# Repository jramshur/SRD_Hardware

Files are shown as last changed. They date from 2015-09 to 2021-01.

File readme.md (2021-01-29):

# SRD Hardware

The simultaneous stimulation-and-recording device (SRD) is a wearable, wireless brain-computer interface system designed to train cortical circuits in awake rats. This repository contains design files for the SRD hardware including Eagle PCB files and 3D design files for the enclosure.

Software and firmware for this hardware system can be found in the following repositories:

- https://github.com/jramshur/SRD_Firmware
- https://github.com/jramshur/SRD_GUI

## Description

The simultaneous stimulation-and-recording device (SRD) is a Bluetooth wireless brain-computer interface system designed for use in awake rats. This repository contains design files for the SRD hardware including Eagle PCB files and 3D design files for the enclosure.

### Features
- Cypress Semiconductor PSoC 3 System-on-a-Chip 
- Intan Technologies digital electrophysiology interface chip
- more ...

### System Overview







## Wiki Navigation

* [Home][home]
* [Circuit Design][circuit]
* [PCB Design][pcb]
* [Enclosure][enclosure]
* [Battery][battery]
* [Programming Adaptor][adaptor]

[home]: https://github.com/jramshur/SRD_Hardware/wiki/Home
[circuit]: https://github.com/jramshur/SRD_Hardware/wiki/Circuit
[pcb]: https://github.com/jramshur/SRD_Hardware/wiki/PCB
[enclosure]: https://github.com/jramshur/SRD_Hardware/wiki/Enclosure
[battery]: https://github.com/jramshur/SRD_Hardware/wiki/Battery
[adaptor]: https://github.com/jramshur/SRD_Hardware/wiki/Programming-Adaptor

## Contact Info

John T. Ramshur, PhD  
jramshur@gmail.com  
LinkedIn: [http://www.linkedin.com/in/johnramshur](http://www.linkedin.com/in/johnramshur)  
Blog: [http://www.johnramshur.com](http://www.johnramshur.com)

**Project was part of my PhD work while at:**

Joint Program in Biomedical Engineering  
[University of Memphis](http://www.memphis.edu/bme/)  
[University of Tennessee Health Science Center](http://www.uthsc.edu/bme/)  
Advisor: Amy de Jongh Curry, PhD

Department of Anatomy and Neurobiology  
[University of Tennessee Health Science Center](https://www.uthsc.edu/anatomy-neurobiology/)  
Advisor: Robert S. Waters, PhD

## License

GNU General Public License 3.0

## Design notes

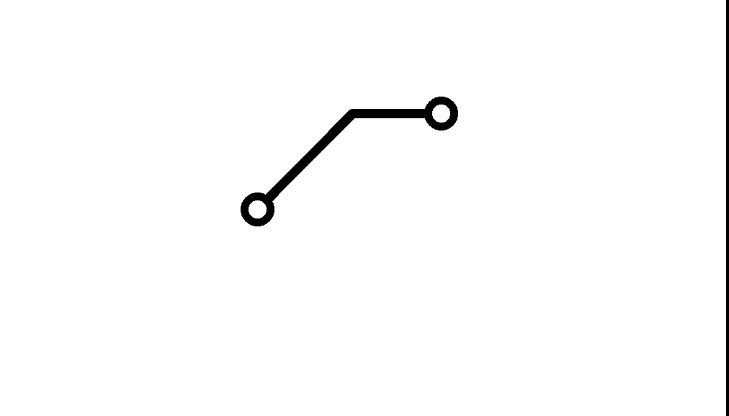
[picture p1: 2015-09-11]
Programming_Adaptor_PCB/eagleUp/.@__thumb/s800eagleUp_PSOC_10pin_to_ZIF_bottom.png

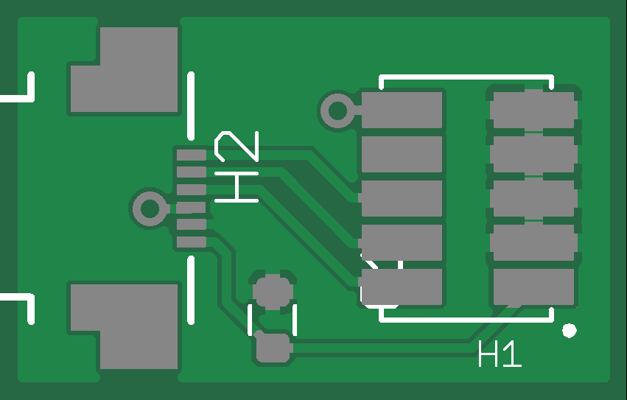
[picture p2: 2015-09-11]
Programming_Adaptor_PCB/eagleUp/.@__thumb/defaulteagleUp_PSOC_10pin_to_ZIF_board_top.png

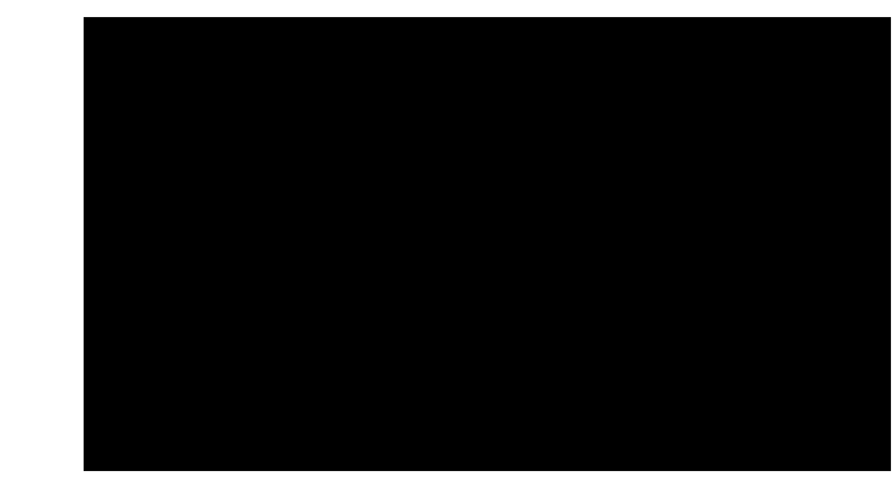
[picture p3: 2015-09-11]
SRD_PCB/eagleUp/eagleUp_SRD_imagesize.png

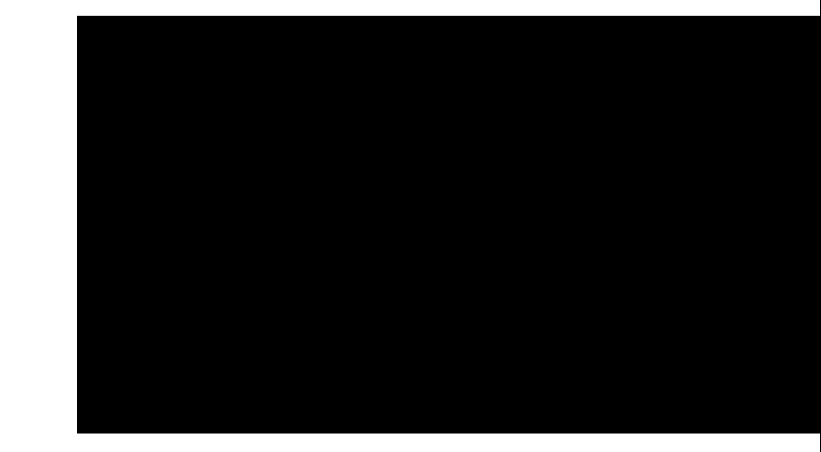
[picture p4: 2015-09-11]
SRD_PCB/eagleUp/.@__thumb/s800eagleUp_SRD_imagesize.png

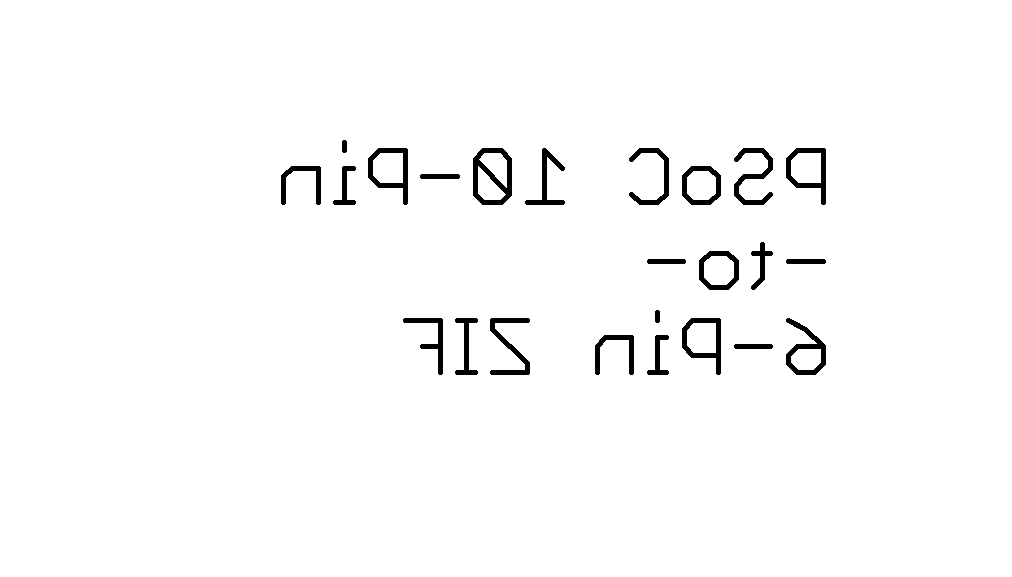
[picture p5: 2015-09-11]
Programming_Adaptor_PCB/eagleUp/eagleUp_PSOC_10pin_to_ZIF_bottom_silk.png

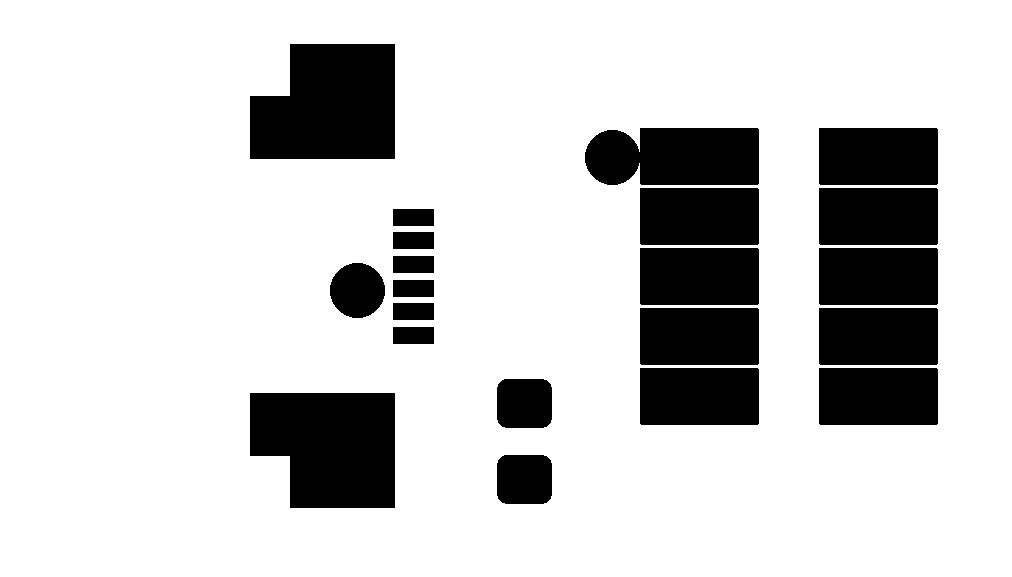
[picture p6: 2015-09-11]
Programming_Adaptor_PCB/eagleUp/eagleUp_PSOC_10pin_to_ZIF_top_mask.png

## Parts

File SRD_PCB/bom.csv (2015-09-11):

Qty | Value | Device | Package | Parts | Description | MF | MPN | OC_FARNELL | OC_NEWARK | PACKAGE | SUPPLIER
1 |  | LED | CHIPLED_0603 | LED1 | LED
1 |  | PHOTOTRANSISTOR | MTD8000M3B-T | Q1 | phototransistor
11 | 0.1uF | CC0402-N | CAPC1005X55N | C20
4 | 0.1uF | CC0603-N | CAPC1608X90N | C7
1 | 10nF | CC0402-N | CAPC1005X55N | C41 | Capacitor (english/metric) cermaic capacitor nominal landpattern (N).
6 | 10uF | CC0805-N | CAPC2012X100N | C12
4 | 1k | RR0402-N | RESC1005X35N | R23
2 | 1uF | CC0402-N | CAPC1005X55N | C23
4 | 1uF | CC0603-N | CAPC1608X90N | C1
1 | 1uF | CC0805-N | CAPC2012X100N | C31 | Capacitor (english/metric) cermaic capacitor nominal landpattern (N).
2 | 2.2uF | CC0603-N | CAPC1608X90N | C5
2 | 220nF | CC0402-N | CAPC1005X55N | C8
2 | 3.3uF | CC0805-N | CAPC2012X100N | C10
4 | 4.7k | RR0402-N | RESC1005X35N | R20
2 | 52746-6 | 52746-6 | 52746-6 | AUX
1 | A79043-001 | A79043-001 | OMNETCS-18PIN-SMD | H10 | Omnetics 18 Position Dual Row Female Nano-Miniature (.025/.64mm) Connector. Featuring 2 Guide Posts Holes and Vertical Surface Mount Tails."
2 | ALD1105 | ALD1105 | SO14MIN | U7
1 | AS1302BGA | AS1302BGA | BGA9C40P3X3_121X121X63B27N | U2
1 | CY8C3866 | CY8C3866 | QFN68_8MM_0.4PITCH | U4
1 | DG9409DN-T1-E4 | DG9409DN-T1-E4 | QFN65P400X400X100-17N | U9 | Analog Multiplexers |  | DG9409DN-T1-E4 | - | 65K2483 | QFN-16 | VISHAY SILICONIX
1 | DIODE | DIODE | DO-216AA | D2 | Diode
1 | LED_RGB | LED_RGB | LED_RGB | RGB1 | Kignbright APTF1616SEJ3ZGGVBDC
1 | MAX865 | MAX865 | UMAX8 | U3
1 | MIC5392/3 | MIC5392/3 | THIN_DFN | U1 | Micrel High-Performance Dual 150mA LDO
1 | PHOTOTRANSISTOR_D | PHOTOTRANSISTOR_D | OP501 | Q2
1 | RHD2216 | RHD2216 | RHD2000 | U6
1 | RN42 | RN42 | RN42 | U5 | Microchip (Roving Networks) RN42 Bluetooth module with antena.
4 | SOLDERJUMPERNO | SOLDERJUMPERNO | SJ_2S-NO | SJ1
1 | SPST_TACT-KMR2 | SPST_TACT-KMR2 | KMR2 | SW1 | SMT 6mm switch
4 | TEST-POINT | TEST-POINT | PAD1MMX1MM | TP10+
1 | USB | USB | USB-MICRO-B-TH | BAT | USB Micro-B Plug

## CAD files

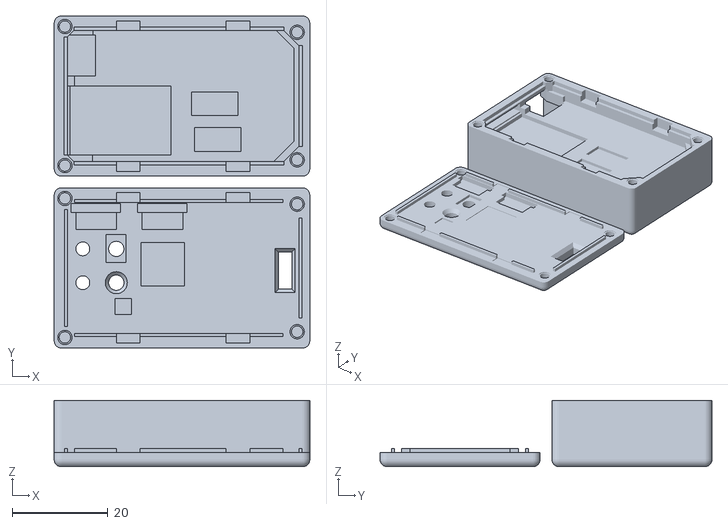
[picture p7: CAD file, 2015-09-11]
enclosure/SRD_revB_caseOnly_for3DPrinting.stl
53.5 x 69.5 x 13.9

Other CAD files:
Programming_Adaptor_PCB/PSOC_10pin_to_ZIF.skp

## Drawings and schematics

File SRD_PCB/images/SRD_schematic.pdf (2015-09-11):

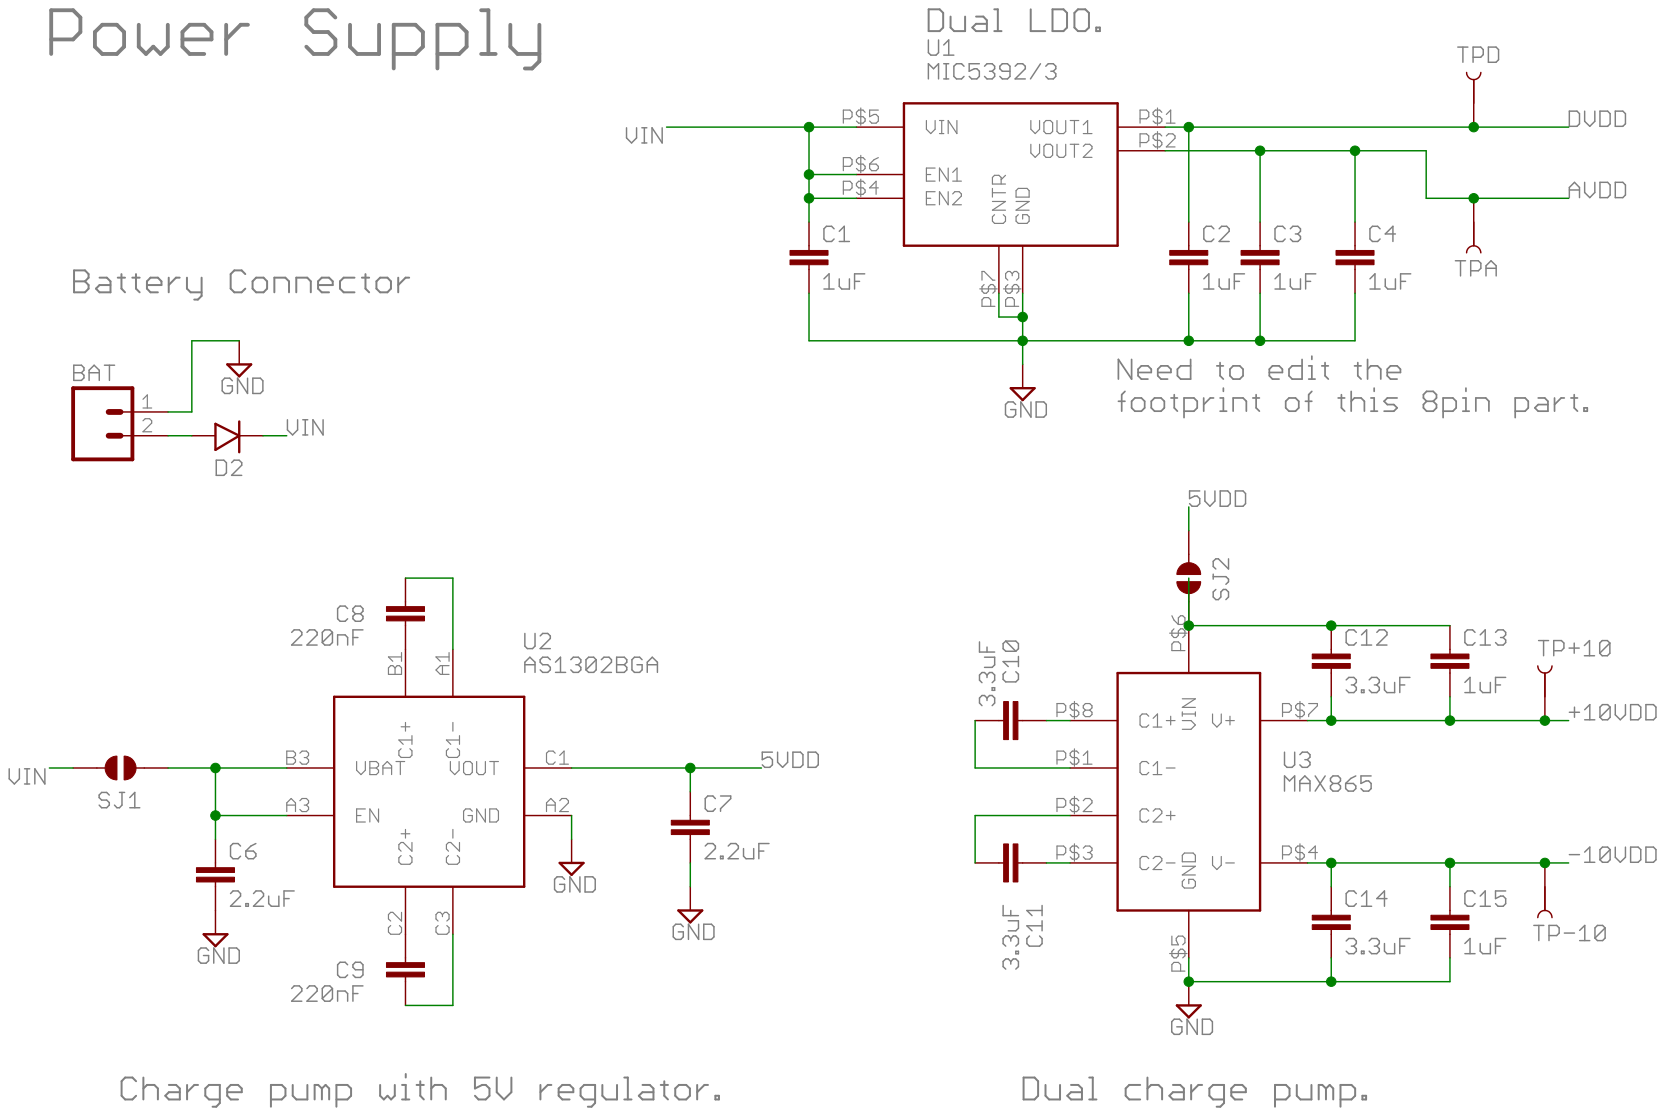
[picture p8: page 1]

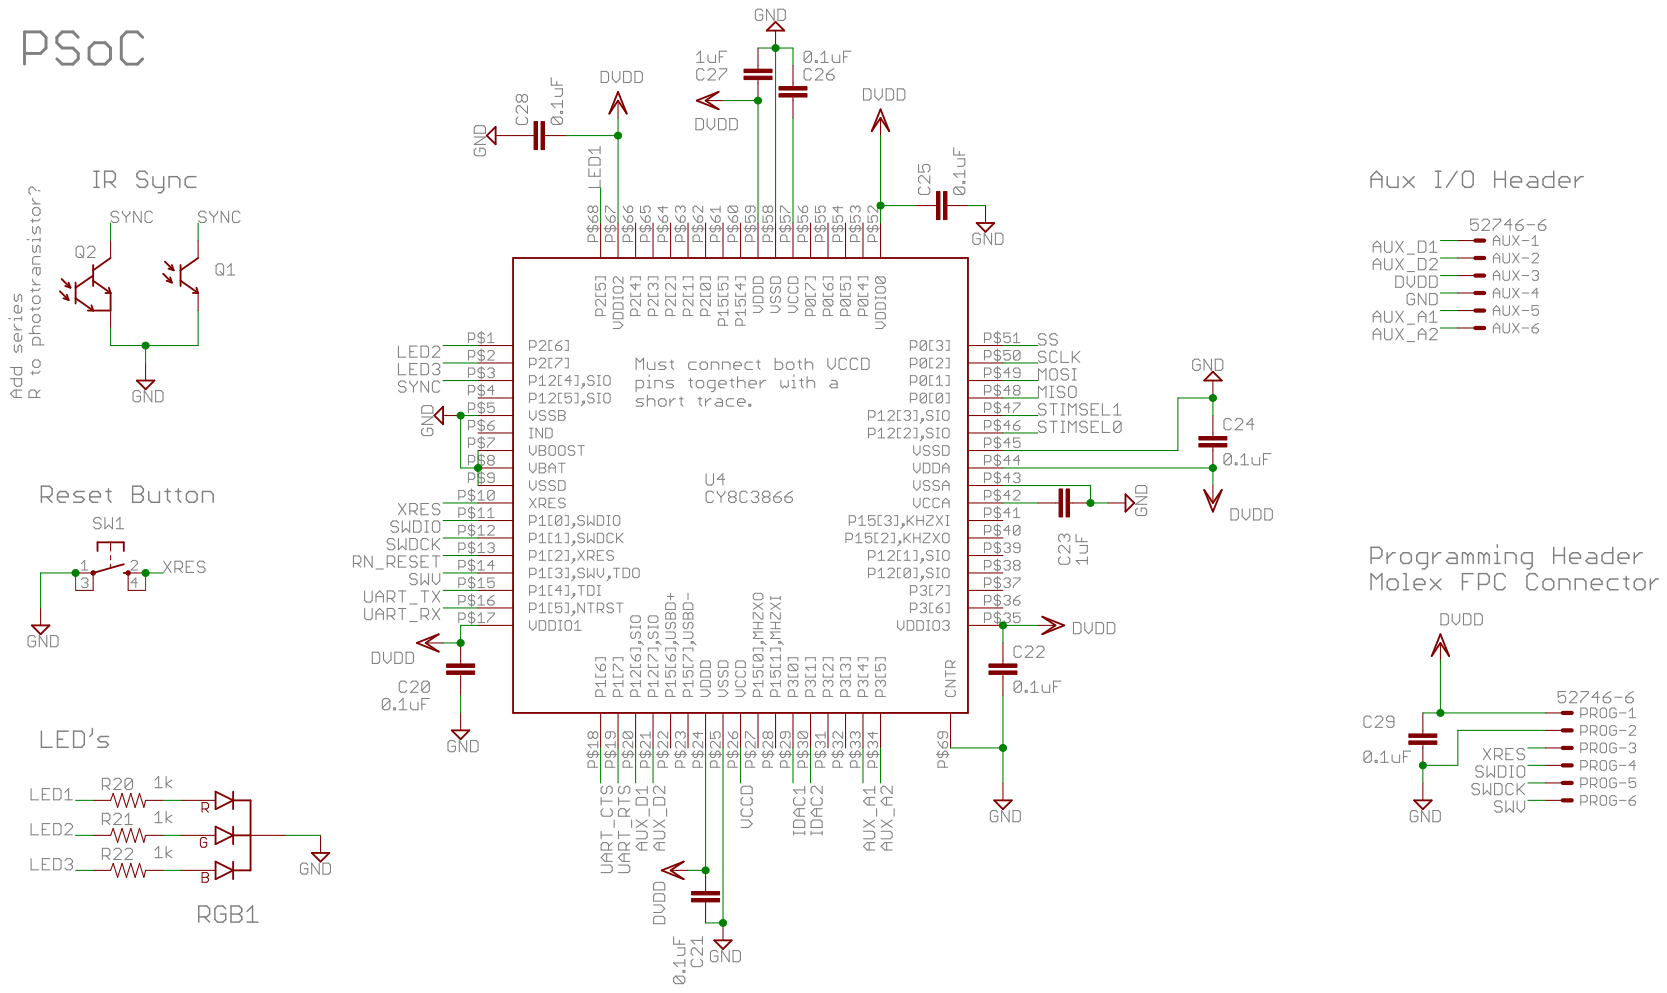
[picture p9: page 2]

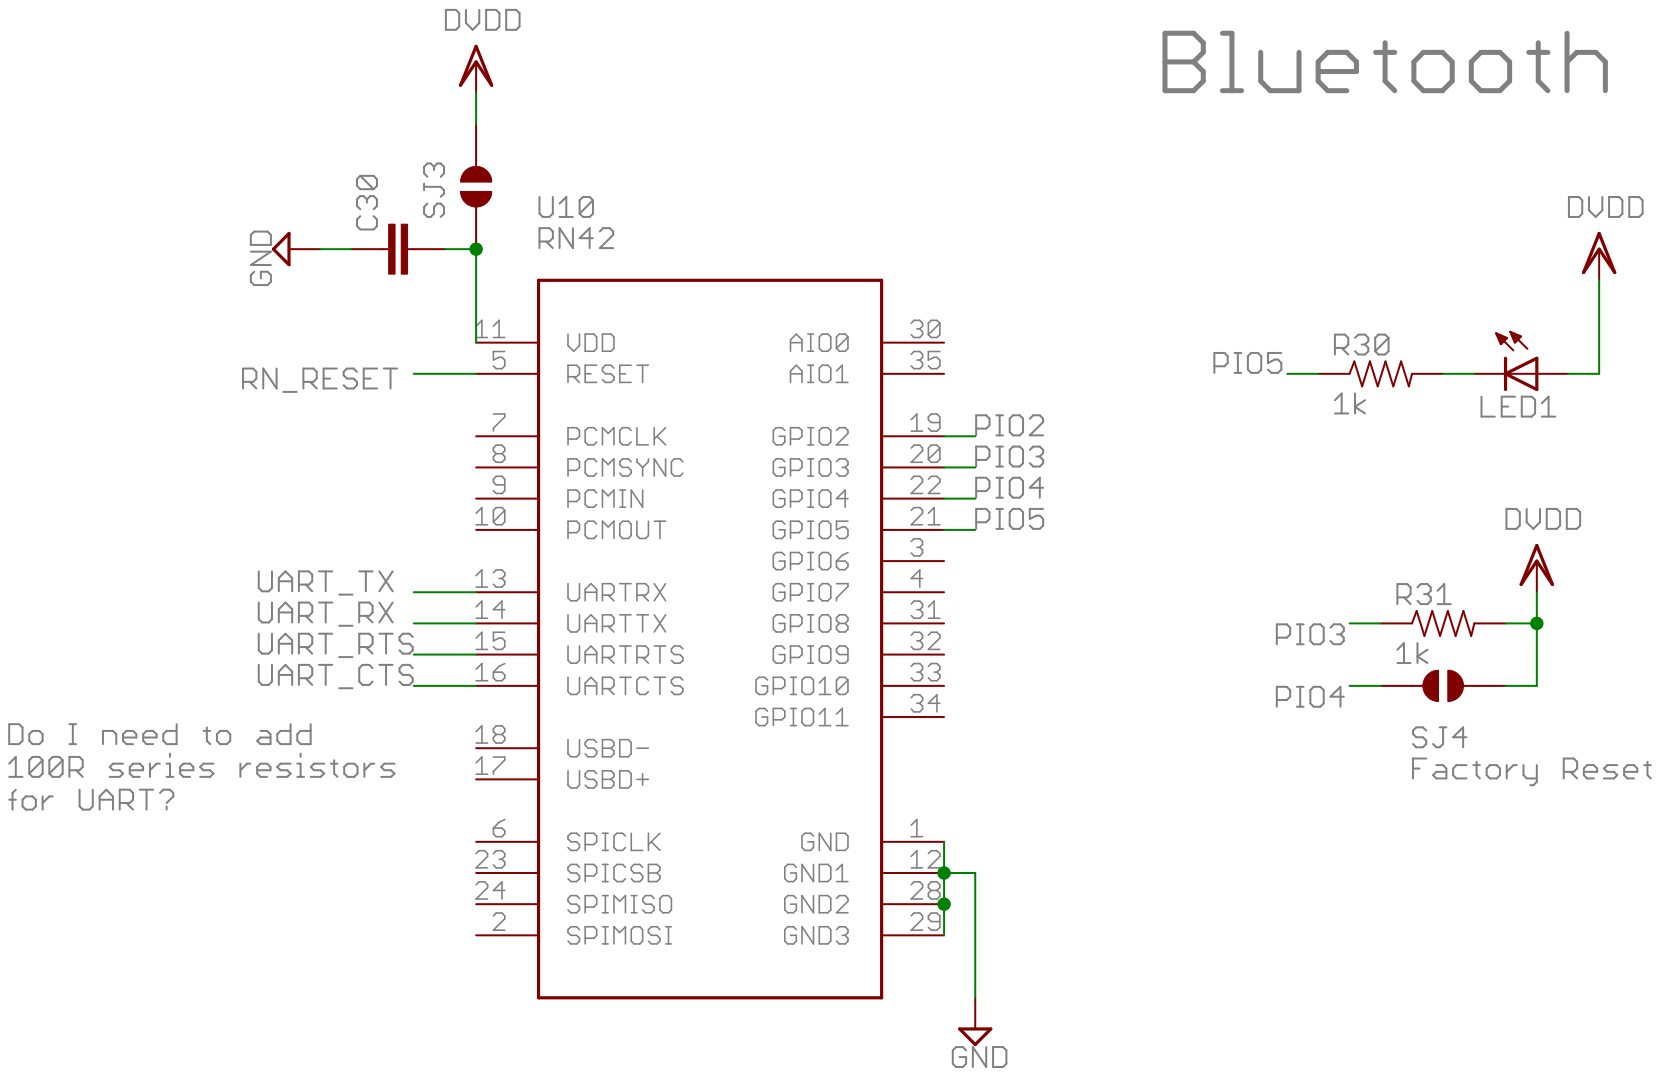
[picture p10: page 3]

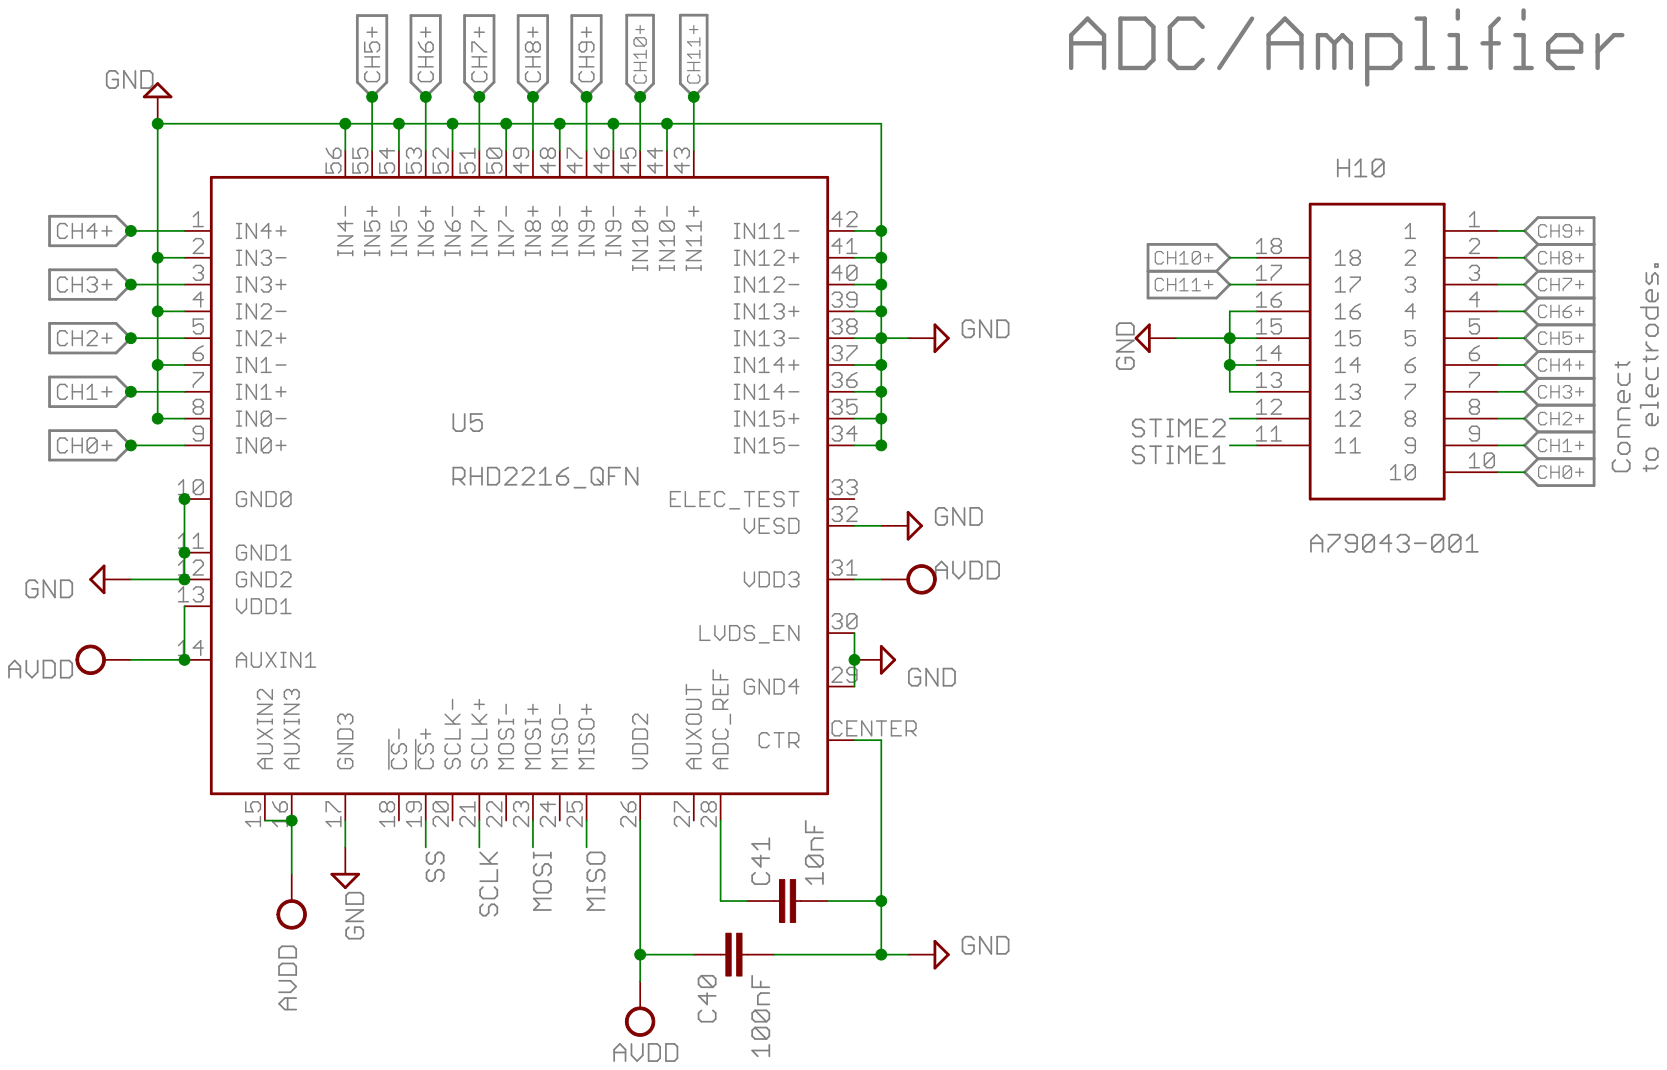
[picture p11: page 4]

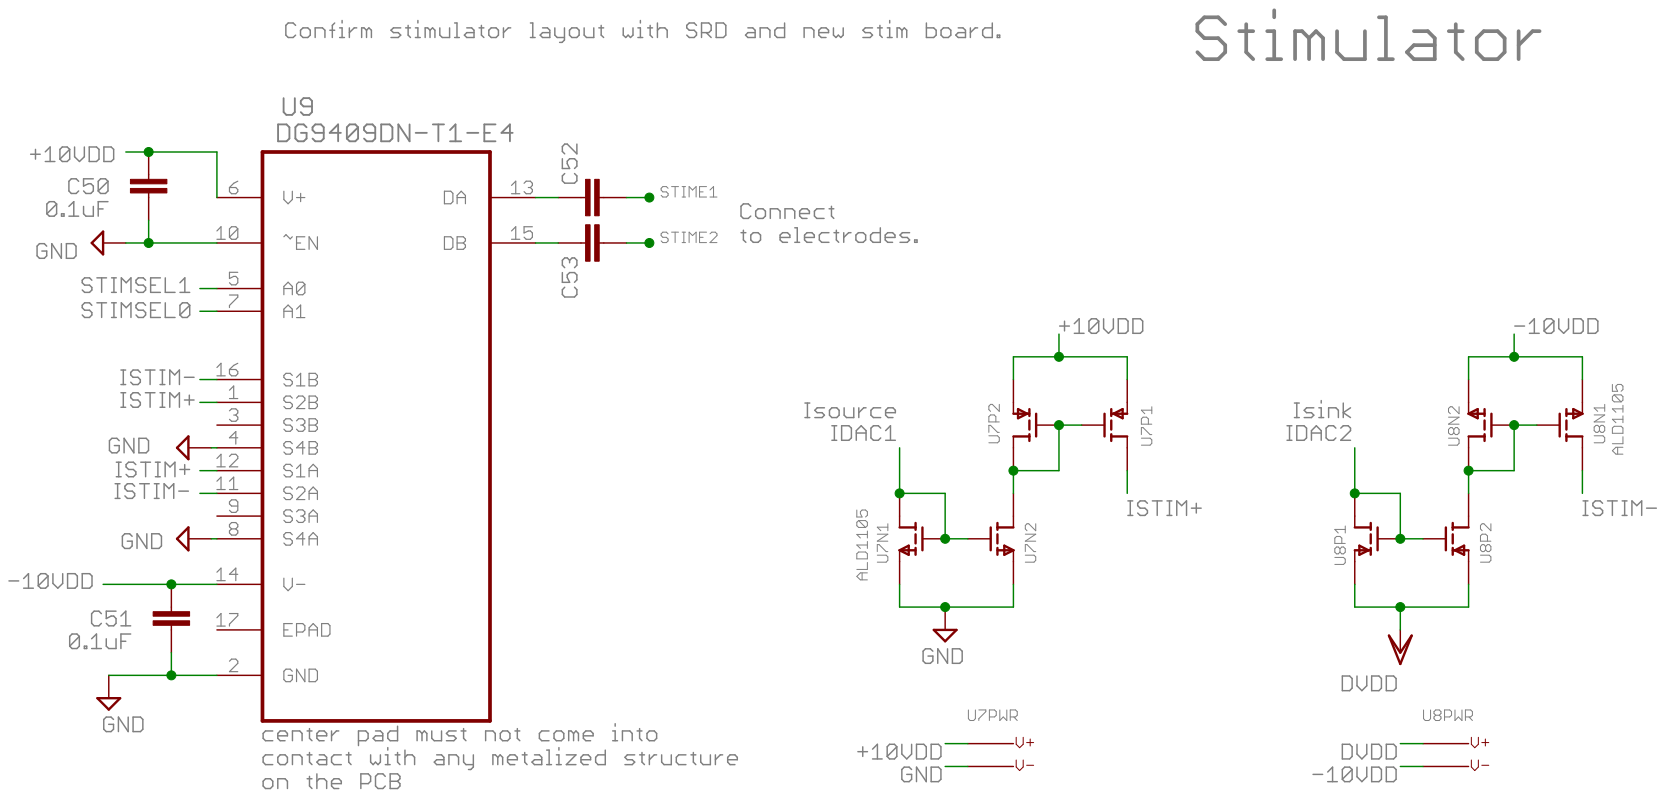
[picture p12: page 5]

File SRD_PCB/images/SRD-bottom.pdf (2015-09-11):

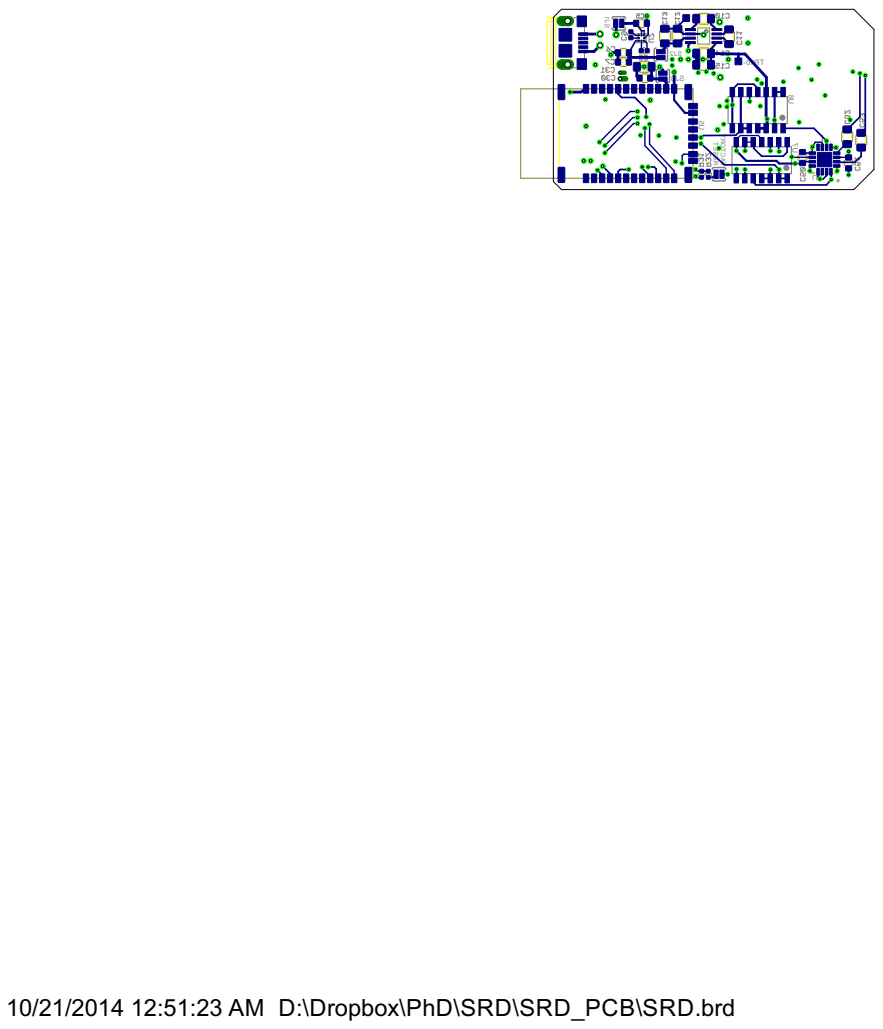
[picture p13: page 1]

10/21/2014 12:51:23 AM D:\Dropbox\PhD\SRD\SRD_PCB\SRD.brd

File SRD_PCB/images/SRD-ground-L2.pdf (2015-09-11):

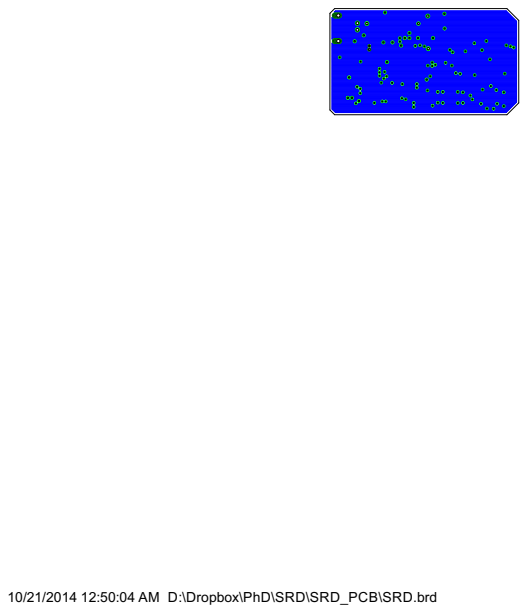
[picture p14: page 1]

10/21/2014 12:50:04 AM D:\Dropbox\PhD\SRD\SRD_PCB\SRD.brd

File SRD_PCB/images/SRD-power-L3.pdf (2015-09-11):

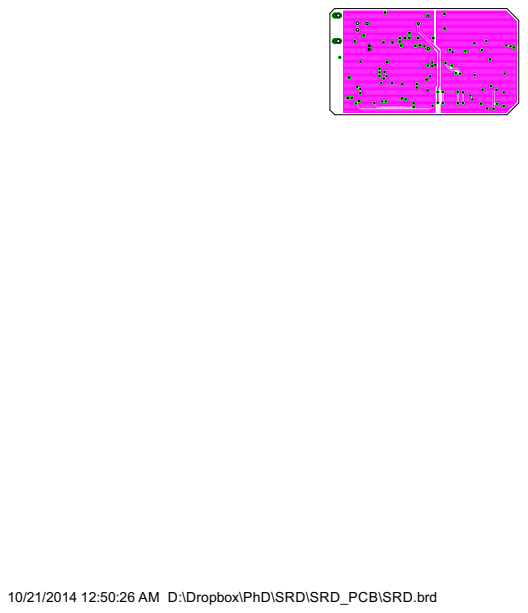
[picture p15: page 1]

10/21/2014 12:50:26 AM D:\Dropbox\PhD\SRD\SRD_PCB\SRD.brd

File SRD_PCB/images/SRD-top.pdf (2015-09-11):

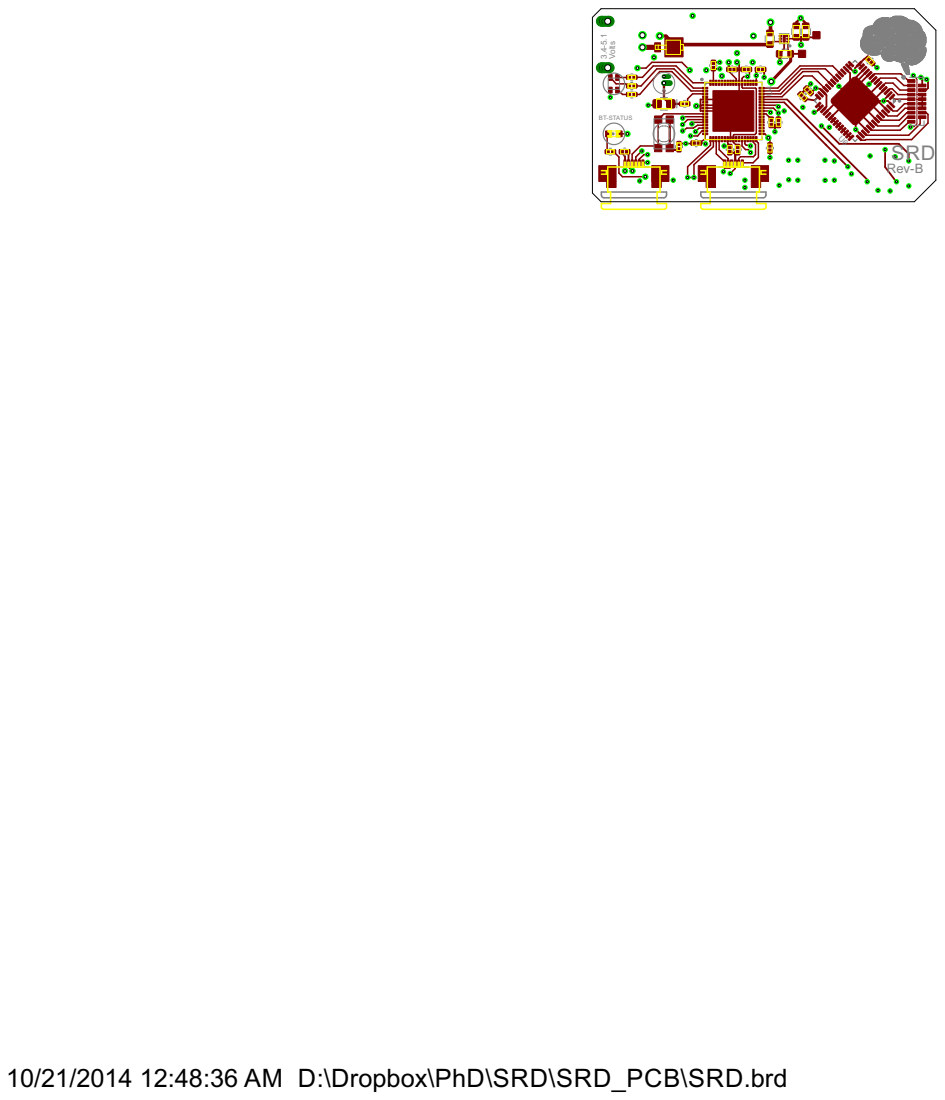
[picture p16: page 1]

10/21/2014 12:48:36 AM D:\Dropbox\PhD\SRD\SRD_PCB\SRD.brd

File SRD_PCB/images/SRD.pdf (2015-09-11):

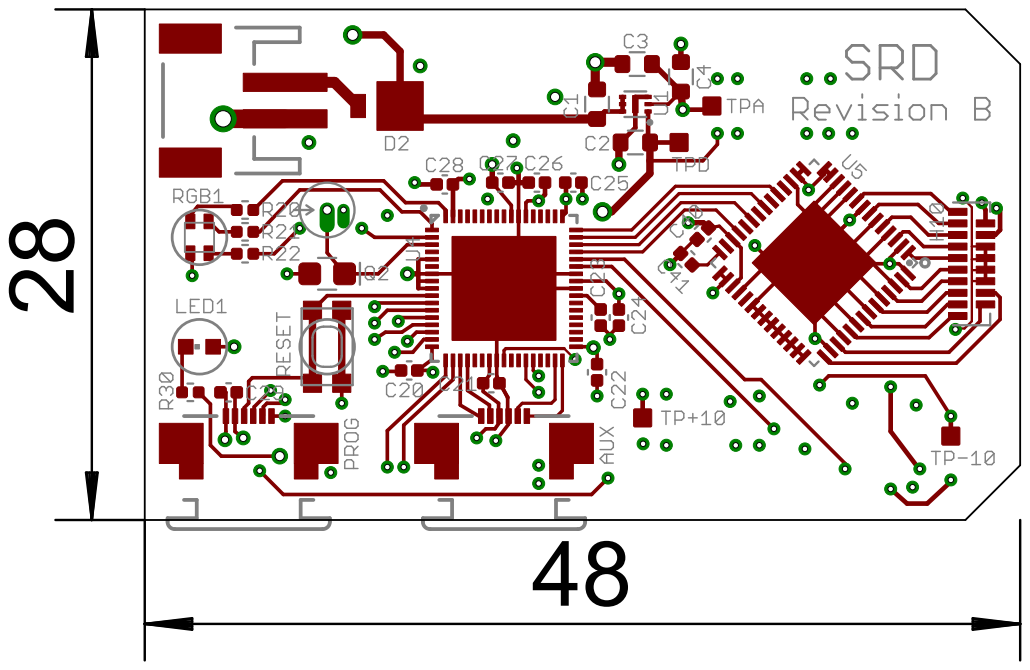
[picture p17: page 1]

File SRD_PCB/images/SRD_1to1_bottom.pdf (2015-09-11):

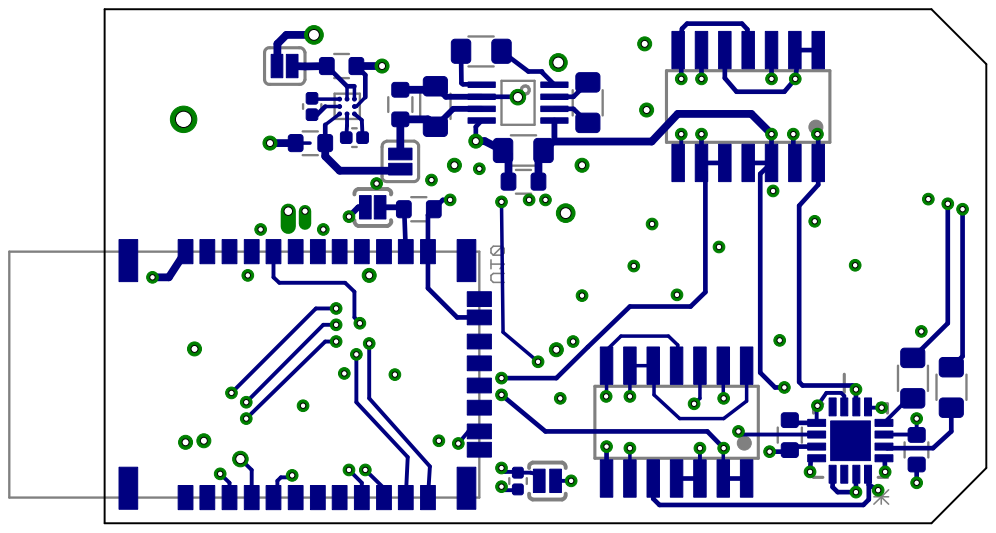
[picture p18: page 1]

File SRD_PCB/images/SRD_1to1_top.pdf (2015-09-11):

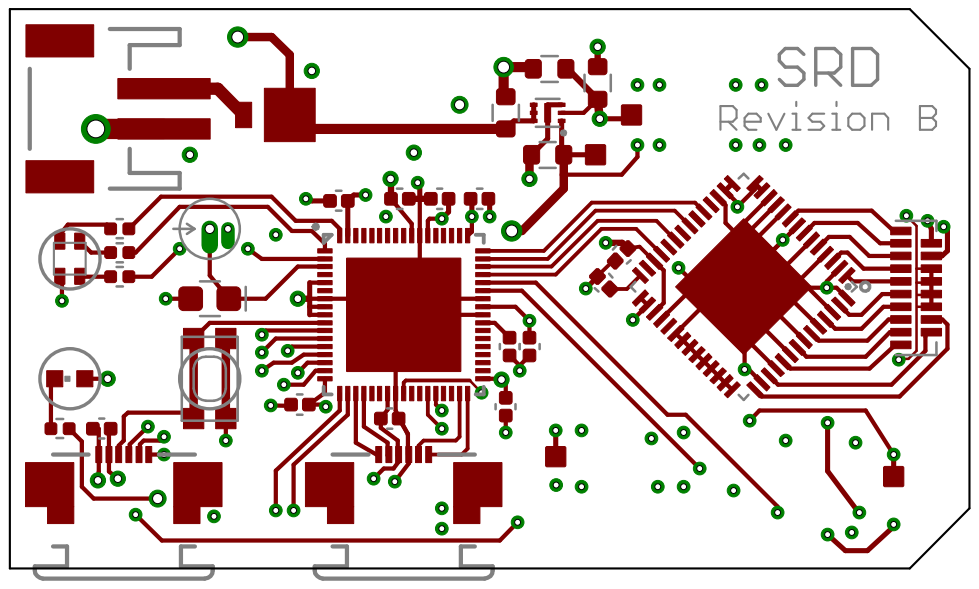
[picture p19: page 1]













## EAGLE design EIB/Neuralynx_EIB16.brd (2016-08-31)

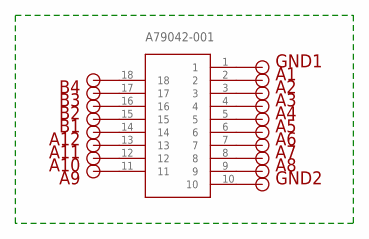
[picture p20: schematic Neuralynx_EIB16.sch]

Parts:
A1, A2, A3, A4, A5, A6, A7, A8, A9, A10, A11, A12: VIA_20MILL; VIA_20MIL
A79042-001: A79043-001; OMNETCS-18PIN-SMD
B1, B2, B3, B4: VIA_20MILL; VIA_20MIL
GND1, GND2: VIA_20MILL; VIA_20MIL

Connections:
unnamed: A79042-001.1, GND1.P$1
unnamed: A79042-001.10, GND2.P$1
unnamed: A8.P$1, A79042-001.9
unnamed: A7.P$1, A79042-001.8
unnamed: A6.P$1, A79042-001.7
unnamed: A5.P$1, A79042-001.6
unnamed: A4.P$1, A79042-001.5
unnamed: A3.P$1, A79042-001.4
unnamed: A2.P$1, A79042-001.3
unnamed: A1.P$1, A79042-001.2
unnamed: A9.P$1, A79042-001.11
unnamed: A10.P$1, A79042-001.12
unnamed: A12.P$1, A79042-001.14
unnamed: A79042-001.15, B1.P$1
unnamed: A79042-001.16, B2.P$1
unnamed: A79042-001.17, B3.P$1
unnamed: A79042-001.18, B4.P$1
unnamed: A11.P$1, A79042-001.13

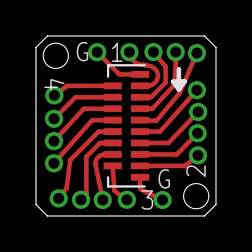
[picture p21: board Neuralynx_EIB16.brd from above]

Board: 2 copper layers, 10.0 x 10.0 mm, 19 parts (0 on the bottom side), 18 nets.

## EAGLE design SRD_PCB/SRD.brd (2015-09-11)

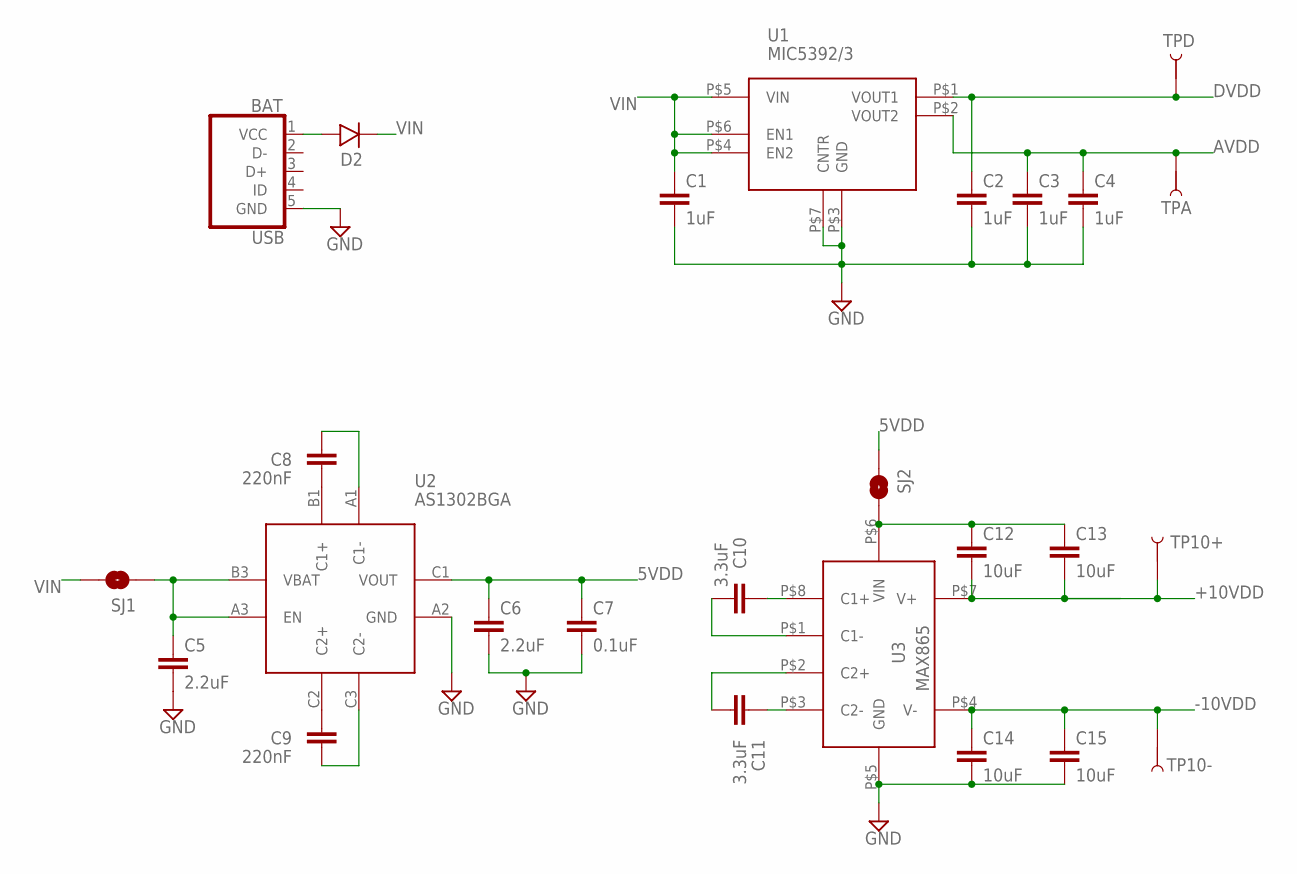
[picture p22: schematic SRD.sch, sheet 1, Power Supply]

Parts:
BAT: USB; USB-MICRO-B-TH
C1, C2, C3, C4: 1uF; CAPC1608X90N
C5, C6: 2.2uF; CAPC1608X90N
C7: 0.1uF; CAPC1608X90N
C8, C9: 220nF; CAPC1005X55N
C10, C11: 3.3uF; CAPC2012X100N
C12, C13, C14, C15: 10uF; CAPC2012X100N
D2: DIODE; DO-216AA
SJ1, SJ2: SOLDERJUMPERNO; SJ_2S-NO
TP10+, TP10-: TEST-POINT; PAD1MMX1MM
TPA: TEST-POINT; PAD1MMX1MM
TPD: TEST-POINT; PAD1MMX1MM
U1: MIC5392/3; THIN_DFN
U2: AS1302BGA; BGA9C40P3X3_121X121X63B27N
U3: MAX865; UMAX8

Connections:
5VDD: C6.1, C7.1, SJ2.1, U2.C1 (VOUT)
+10VDD: C12.2, C13.2, TP10+.P$1, U3.P$7 (V+); also elsewhere on the board
-10VDD: C14.1, C15.1, TP10-.P$1, U3.P$4 (V-); also elsewhere on the board
AVDD: C3.1, C4.1, TPA.P$1, U1.P$2 (VOUT2); also elsewhere on the board
DVDD: C2.1, TPD.P$1, U1.P$1 (VOUT1); also elsewhere on the board
GND: BAT.5 (GND), C1.2, C2.2, C3.2, C4.2, C5.2, C6.2, C7.2, C14.2, C15.2, U1.P$3 (GND), U1.P$7 (CNTR), U2.A2 (GND), U3.P$5 (GND); also elsewhere on the board
unnamed: C5.1, SJ1.1, U2.A3 (EN), U2.B3 (VBAT)
unnamed: C12.1, C13.1, SJ2.2, U3.P$6 (VIN)
unnamed: C8.1, U2.A1 (C1-)
unnamed: C9.2, U2.C3 (C2-)
unnamed: C11.1, U3.P$3 (C2-)
unnamed: C11.2, U3.P$2 (C2+)
unnamed: C10.1, U3.P$8 (C1+)
unnamed: C10.2, U3.P$1 (C1-)
unnamed: C8.2, U2.B1 (C1+)
unnamed: C9.1, U2.C2 (C2+)
VBAT: BAT.1 (VCC), D2.A
VIN: C1.1, D2.C, SJ1.2, U1.P$4 (EN2), U1.P$5 (VIN), U1.P$6 (EN1)

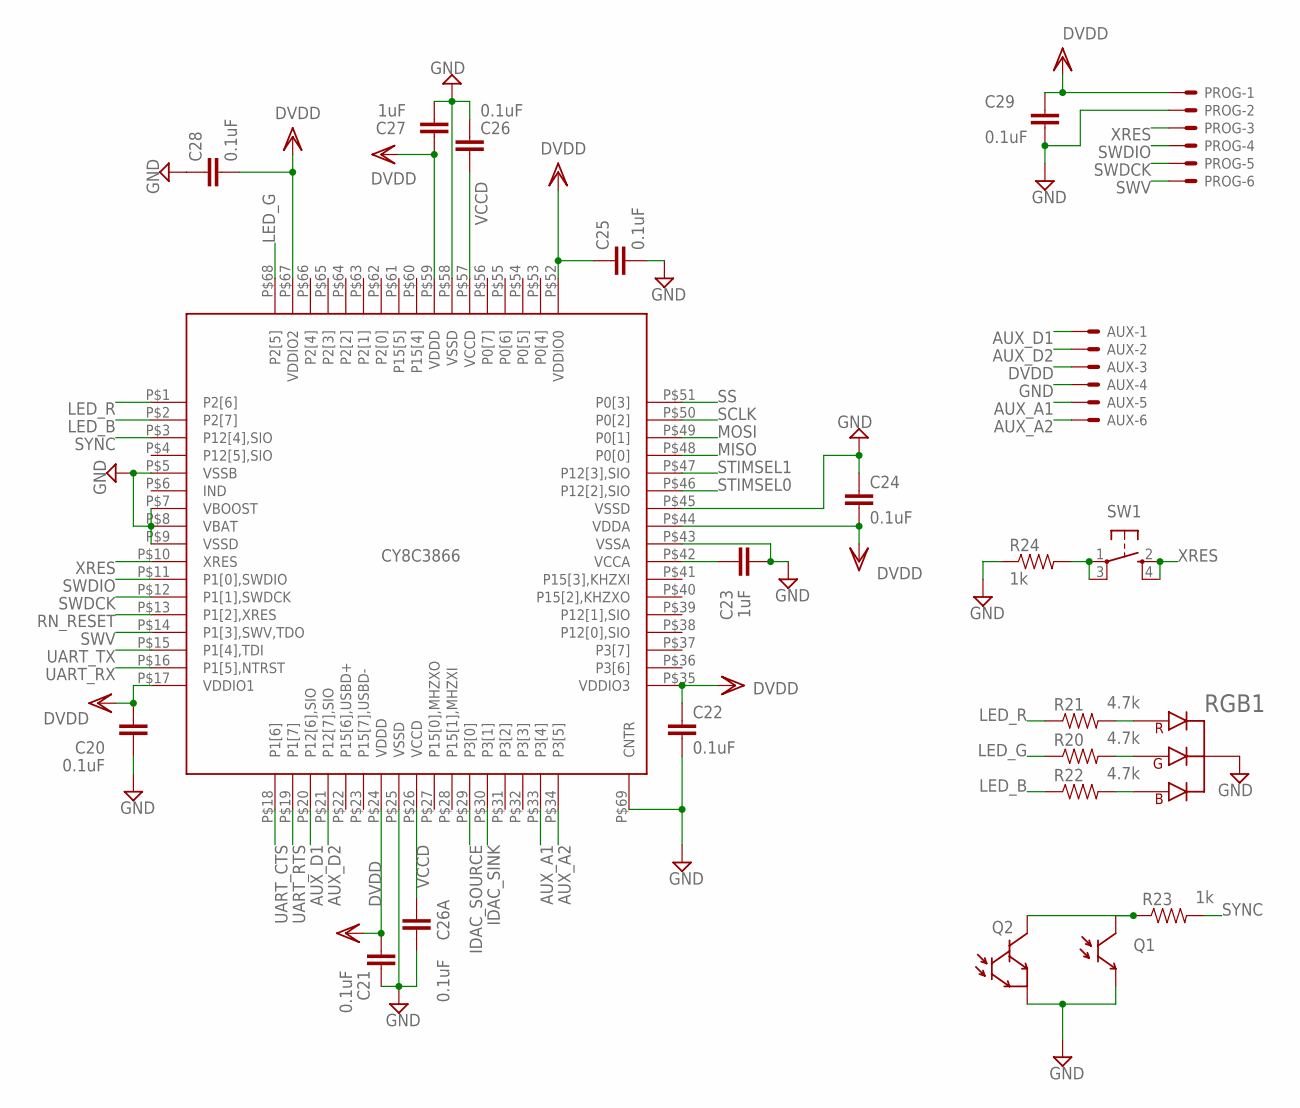
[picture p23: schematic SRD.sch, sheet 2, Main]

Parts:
AUX: 52746-6
C20, C21, C22, C24, C25, C26, C26A, C28, C29: 0.1uF; CAPC1005X55N
C23, C27: 1uF; CAPC1005X55N
PROG: 52746-6
Q1: PHOTOTRANSISTOR; MTD8000M3B-T
Q2: PHOTOTRANSISTOR_D; OP501
R20, R21, R22: 4.7k; RESC1005X35N
R23, R24: 1k; RESC1005X35N
RGB1: LED_RGB
SW1: SPST_TACT-KMR2; KMR2
U4: CY8C3866; QFN68_8MM_0.4PITCH

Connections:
AUX_A1: AUX.5, U4.P$33 (P3[4])
AUX_A2: AUX.6, U4.P$34 (P3[5])
AUX_D1: AUX.1, U4.P$20 (P12[6],SIO)
AUX_D2: AUX.2, U4.P$21 (P12[7],SIO)
DVDD: AUX.3, C20.1, C21.1, C22.1, C24.2, C25.1, C27.1, C28.2, C29.1, PROG.1, U4.P$17 (VDDIO1), U4.P$24 (VDDD), U4.P$35 (VDDIO3), U4.P$44 (VDDA), U4.P$52 (VDDIO0), U4.P$59 (VDDD), U4.P$67 (VDDIO2); also elsewhere on the board
GND: AUX.4, C20.2, C21.2, C22.2, C23.2, C24.1, C25.2, C26.2, C26A.1, C27.2, C28.1, C29.2, PROG.2, Q1.E, Q2.E, R24.1, RGB1.P$1 (COM), U4.P$5 (VSSB), U4.P$7 (VBOOST), U4.P$8 (VBAT), U4.P$9 (VSSD), U4.P$25 (VSSD), U4.P$43 (VSSA), U4.P$45 (VSSD), U4.P$58 (VSSD), U4.P$69 (CNTR); also elsewhere on the board
IDAC_SINK: U4.P$30 (P3[1]); also elsewhere on the board
IDAC_SOURCE: U4.P$29 (P3[0]); also elsewhere on the board
LED_B: R22.1, U4.P$2 (P2[7])
LED_G: R20.1, U4.P$68 (P2[5])
LED_R: R21.1, U4.P$1 (P2[6])
MISO: U4.P$48 (P0[0]); also elsewhere on the board
MOSI: U4.P$49 (P0[1]); also elsewhere on the board
unnamed: R21.2, RGB1.P$2 (R)
unnamed: R20.2, RGB1.P$3 (G)
unnamed: R22.2, RGB1.P$4 (B)
unnamed: Q1.C, Q2.C, R23.1
unnamed: R24.2, SW1.1, SW1.3 (P1)
unnamed: C23.1, U4.P$42 (VCCA)
RN_RESET: U4.P$13 (P1[2],XRES); also elsewhere on the board
SCLK: U4.P$50 (P0[2]); also elsewhere on the board
SS: U4.P$51 (P0[3]); also elsewhere on the board
STIMSEL0: U4.P$46 (P12[2],SIO); also elsewhere on the board
STIMSEL1: U4.P$47 (P12[3],SIO); also elsewhere on the board
SWDCK: PROG.5, U4.P$12 (P1[1],SWDCK)
SWDIO: PROG.4, U4.P$11 (P1[0],SWDIO)
SWV: PROG.6, U4.P$14 (P1[3],SWV,TDO)
SYNC: R23.2, U4.P$3 (P12[4],SIO)
UART_CTS: U4.P$18 (P1[6]); also elsewhere on the board
UART_RTS: U4.P$19 (P1[7]); also elsewhere on the board
UART_RX: U4.P$16 (P1[5],NTRST); also elsewhere on the board
UART_TX: U4.P$15 (P1[4],TDI); also elsewhere on the board
VCCD: C26.1, C26A.2, U4.P$26 (VCCD), U4.P$57 (VCCD)
XRES: PROG.3, SW1.2 (S), SW1.4 (S1), U4.P$10 (XRES)

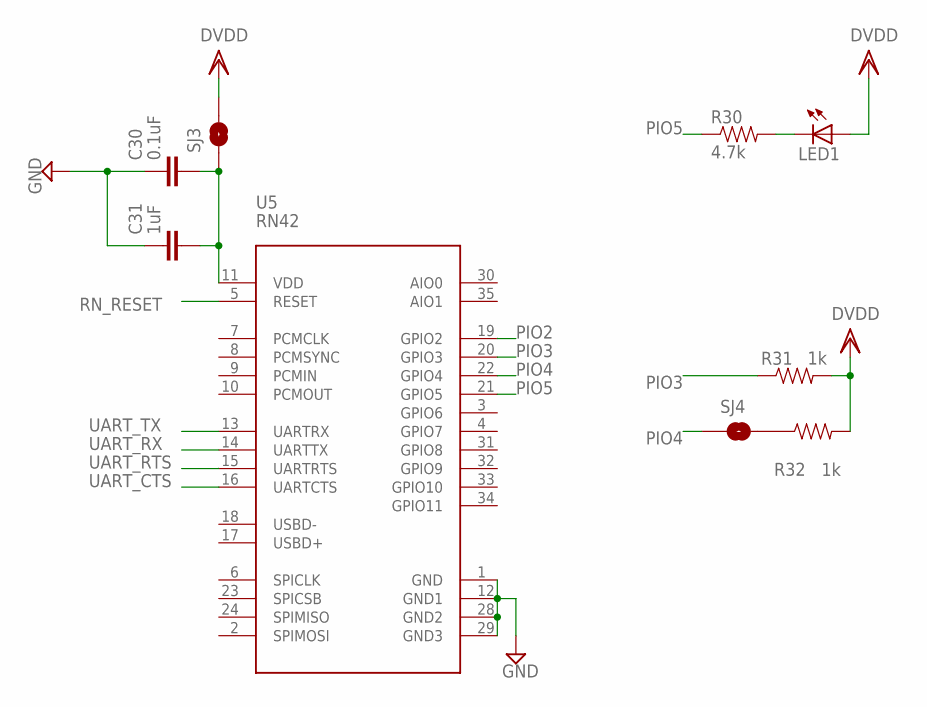
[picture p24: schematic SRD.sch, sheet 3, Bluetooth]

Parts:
C30: 0.1uF; CAPC1608X90N
C31: 1uF; CAPC2012X100N
LED1: LED; CHIPLED_0603
R30: 4.7k; RESC1005X35N
R31, R32: 1k; RESC1005X35N
SJ3, SJ4: SOLDERJUMPERNO; SJ_2S-NO
U5: RN42

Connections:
DVDD: LED1.A, R31.2, R32.2, SJ3.2; also elsewhere on the board
GND: C30.1, C31.1, U5.1 (GND), U5.12 (GND1), U5.28 (GND2), U5.29 (GND3); also elsewhere on the board
unnamed: LED1.C, R30.2
unnamed: C30.2, C31.2, SJ3.1, U5.11 (VDD)
unnamed: R32.1, SJ4.2
PIO2: U5.19 (GPIO2)
PIO3: R31.1, U5.20 (GPIO3)
PIO4: SJ4.1, U5.22 (GPIO4)
PIO5: R30.1, U5.21 (GPIO5)
RN_RESET: U5.5 (RESET); also elsewhere on the board
UART_CTS: U5.16 (UARTCTS); also elsewhere on the board
UART_RTS: U5.15 (UARTRTS); also elsewhere on the board
UART_RX: U5.14 (UARTTX); also elsewhere on the board
UART_TX: U5.13 (UARTRX); also elsewhere on the board

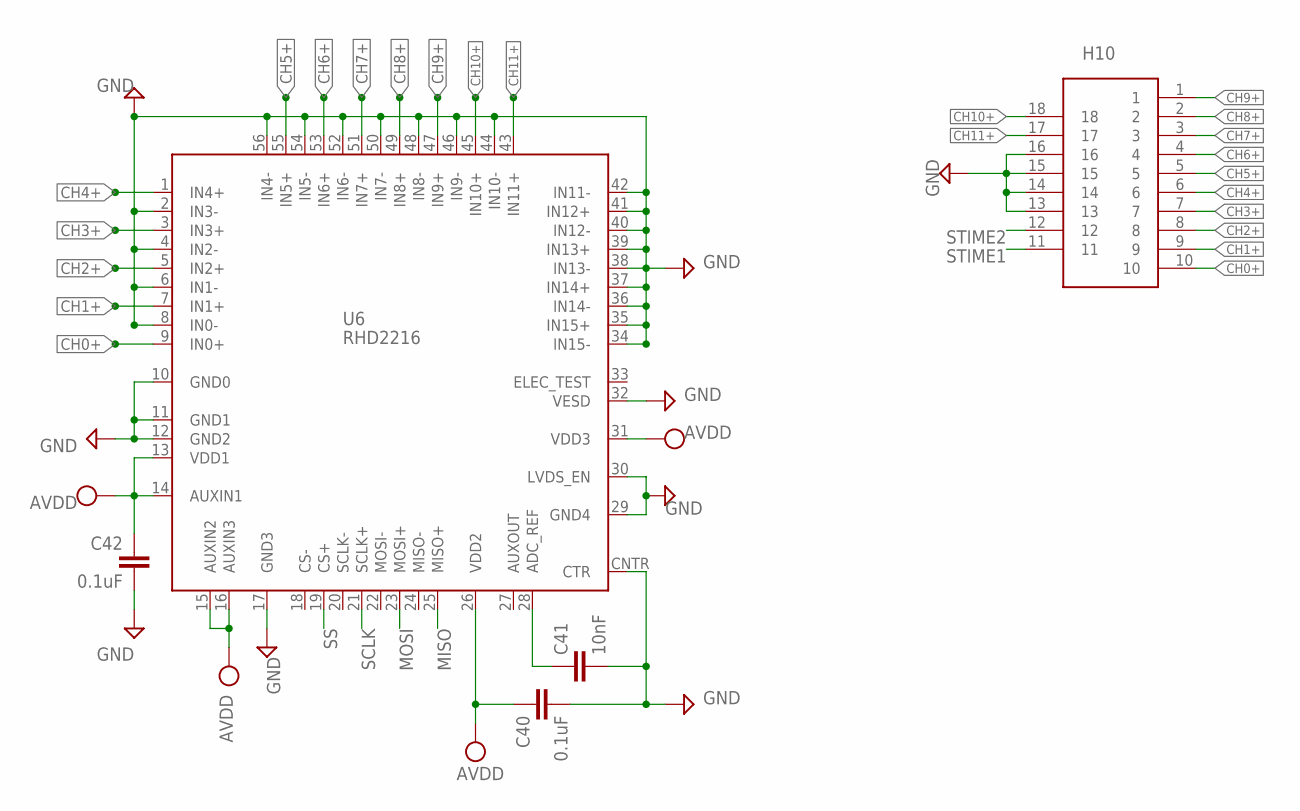
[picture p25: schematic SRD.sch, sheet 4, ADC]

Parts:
C40, C42: 0.1uF; CAPC1005X55N
C41: 10nF; CAPC1005X55N
H10: A79043-001; OMNETCS-18PIN-SMD
U6: RHD2216; RHD2000

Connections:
AVDD: C40.1, C42.1, U6.13 (VDD1), U6.14 (AUXIN1), U6.15 (AUXIN2), U6.16 (AUXIN3), U6.26 (VDD2), U6.31 (VDD3); also elsewhere on the board
CH0+: H10.10, U6.9 (IN0+)
CH1+: H10.9, U6.7 (IN1+)
CH2+: H10.8, U6.5 (IN2+)
CH3+: H10.7, U6.3 (IN3+)
CH4+: H10.6, U6.1 (IN4+)
CH5+: H10.5, U6.55 (IN5+)
CH6+: H10.4, U6.53 (IN6+)
CH7+: H10.3, U6.51 (IN7+)
CH8+: H10.2, U6.49 (IN8+)
CH9+: H10.1, U6.47 (IN9+)
CH10+: H10.18, U6.45 (IN10+)
CH11+: H10.17, U6.43 (IN11+)
GND: C40.2, C41.2, C42.2, H10.13, H10.14, H10.15, H10.16, U6.2 (IN3-), U6.4 (IN2-), U6.6 (IN1-), U6.8 (IN0-), U6.10 (GND0), U6.11 (GND1), U6.12 (GND2), U6.17 (GND3), U6.29 (GND4), U6.30 (LVDS_EN), U6.32 (VESD), U6.34 (IN15-), U6.35 (IN15+), U6.36 (IN14-), U6.37 (IN14+), U6.38 (IN13-), U6.39 (IN13+), U6.40 (IN12-), U6.41 (IN12+), U6.42 (IN11-), U6.44 (IN10-), U6.46 (IN9-), U6.48 (IN8-), U6.50 (IN7-), U6.52 (IN6-), U6.54 (IN5-), U6.56 (IN4-), U6.CNTR (CTR); also elsewhere on the board
MISO: U6.25 (MISO+); also elsewhere on the board
MOSI: U6.23 (MOSI+); also elsewhere on the board
unnamed: C41.1, U6.28 (ADC_REF)
SCLK: U6.21 (SCLK+); also elsewhere on the board
SS: U6.19 (CS+); also elsewhere on the board
STIME1: H10.11; also elsewhere on the board
STIME2: H10.12; also elsewhere on the board

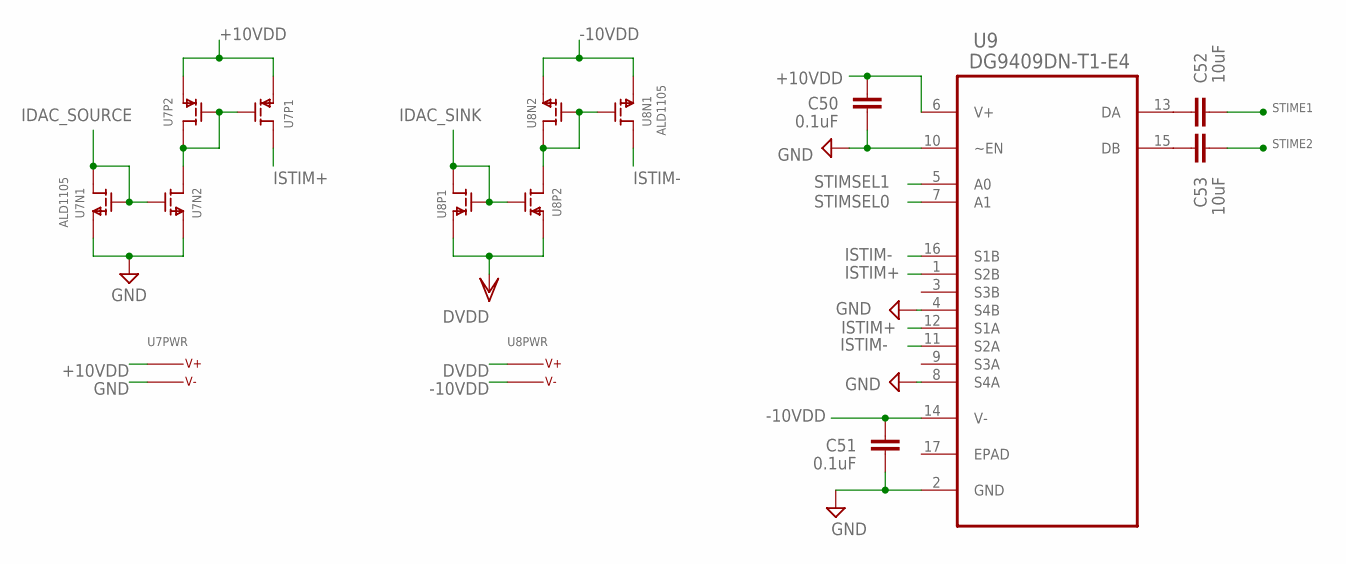
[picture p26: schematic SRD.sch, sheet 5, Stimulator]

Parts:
C50, C51: 0.1uF; CAPC1608X90N
C52, C53: 10uF; CAPC2012X100N
U7, U8: ALD1105; SO14MIN
U9: DG9409DN-T1-E4; QFN65P400X400X100-17N

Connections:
+10VDD: C50.1, U7.7 (S), U7.8 (S), U7.11 (V+), U9.6 (V+); also elsewhere on the board
-10VDD: C51.1, U8.3 (S), U8.4 (V-), U8.12 (S), U9.14 (V-); also elsewhere on the board
DVDD: U8.7 (S), U8.8 (S), U8.11 (V+); also elsewhere on the board
GND: C50.2, C51.2, U7.3 (S), U7.4 (V-), U7.12 (S), U9.2 (GND), U9.4 (S4B), U9.8 (S4A), U9.10 (~EN); also elsewhere on the board
IDAC_SINK: U8.5 (D), U8.6 (G), U8.9 (G); also elsewhere on the board
IDAC_SOURCE: U7.1 (D), U7.2 (G), U7.13 (G); also elsewhere on the board
ISTIM+: U7.5 (D), U9.1 (S2B), U9.12 (S1A)
ISTIM-: U8.1 (D), U9.11 (S2A), U9.16 (S1B)
unnamed: C52.1, U9.13 (DA)
unnamed: U7.6 (G), U7.9 (G), U7.10 (D), U7.14 (D)
unnamed: C53.1, U9.15 (DB)
unnamed: U8.2 (G), U8.10 (D), U8.13 (G), U8.14 (D)
STIME1: C52.2; also elsewhere on the board
STIME2: C53.2; also elsewhere on the board
STIMSEL0: U9.7 (A1); also elsewhere on the board
STIMSEL1: U9.5 (A0); also elsewhere on the board

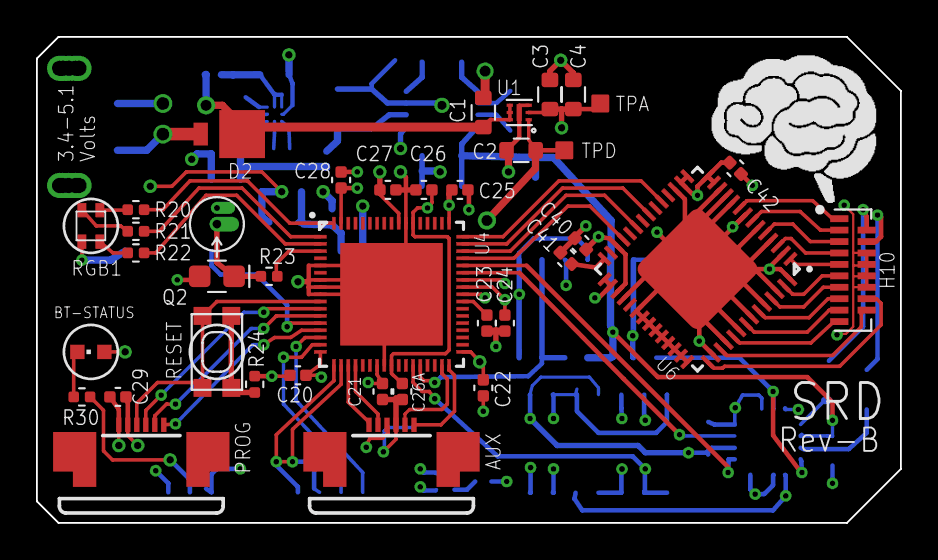
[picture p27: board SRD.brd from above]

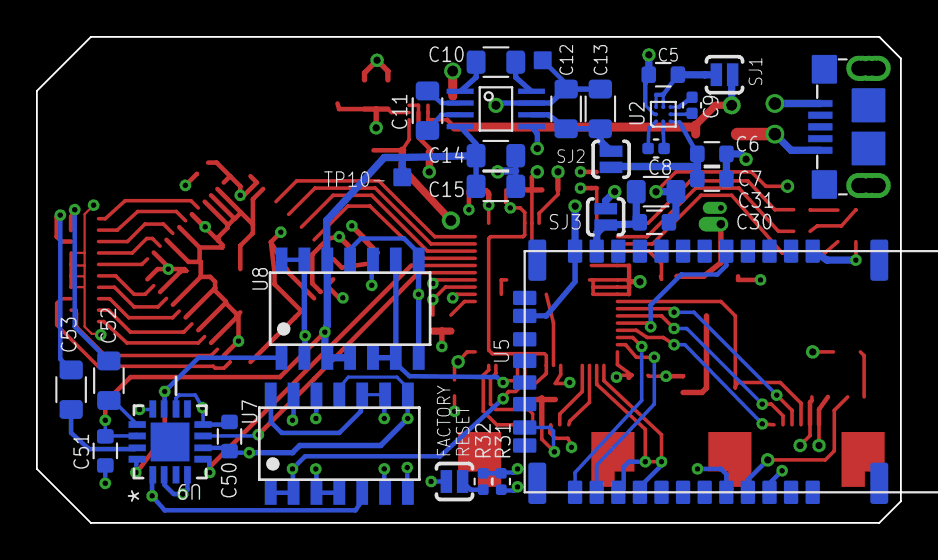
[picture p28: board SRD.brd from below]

Board: 4 copper layers, 48.0 x 27.0 mm, 71 parts (32 on the bottom side), 77 nets.

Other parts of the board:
U$1: LOGO_BRAIN

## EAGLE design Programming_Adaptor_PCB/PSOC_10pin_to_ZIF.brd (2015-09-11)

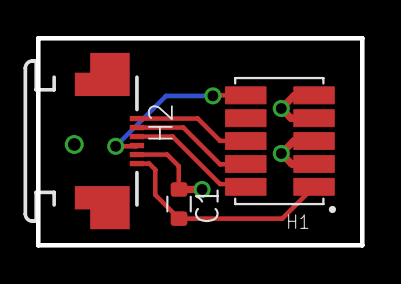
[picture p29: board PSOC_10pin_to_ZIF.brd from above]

Board: 2 copper layers, 18.0 x 11.5 mm, 3 parts (0 on the bottom side), 6 nets.

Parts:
C1: 0.1uF; CAPC1608X90N
H1: 2X5_SMD_HEADER_1.27MM
H2: 52746-6

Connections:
GND: C1.1, H1.P$3, H1.P$5, H1.P$7, H1.P$9, H2.5
SWDCK: H1.P$4, H2.2
SWDIO: H1.P$2, H2.3
SWV: H1.P$6, H2.1
VDD: C1.2, H1.P$1, H2.6
XRES: H1.P$10, H2.4

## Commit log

2015-09-11 Initial post-graduate commit
    [PSOC_10pin_to_ZIF.brd, PSOC_10pin_to_ZIF.sch, PSOC_10pin_to_ZIF.skp, SRD.brd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]
2015-09-13 Added pics
    [PSOC_10pin_to_ZIF.sch]
2016-08-31 Quick update
    [Neuralynx_EIB16.brd, Neuralynx_EIB16.sch]
2016-12-21 Reorganized files
    [SRD_revB_caseOnly_for3DPrinting.stl, SRD_revB_caseOnly_forPrinting.stl]
